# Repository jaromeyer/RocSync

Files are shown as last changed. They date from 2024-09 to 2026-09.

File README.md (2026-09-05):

# RocSync: Temporal Multi-Camera Synchronization

> [!WARNING]
> **This repository is deprecated and no longer maintained.**
> Development has moved to a new fork, which will continue to be updated:
> 👉 **[BAL-ROCS-BUT-COOL/RocSync](https://github.com/BAL-ROCS-BUT-COOL/RocSync)**

RocSync Front

**RocSync**  is an open-source solution for millisecond-accurate temporal synchronization of multiple cameras. The core component is a 25x25 cm PCB featuring 100 dual LEDs (each consisting of a visible red LED and an infrared LED) arranged in a circle and 16 additional dual LEDs to display a binary counter. There is always exactly one illuminated LED in the circle and it advances one step every millisecond, while the binary display counts the number of complete rotations. The second part is a Python application that decodes images and videos of the device and provides exact timestamps (relative to the RocSync device's internal clock) for every frame. It supports synchronization of both standard RGB cameras (e.g., Kinect, GoPro, Canon) and specialized IR tracking cameras, such as the [Atracsys fusionTrack 500](https://atracsys.com/fusiontrack-500/), making it ideal for research and applications requiring high-precision multi-camera setups.

## Repository Structure

This repository contains three main sections, each with its own README:

- **`hw/`**: KiCad files for PCB design and CAD models.
- **`fw/`**: PlatformIO project for microcontroller firmware.
- **`sw/`**: Python source code for computer vision processing.

## Getting Started

For detailed instructions on setting up and using RocSync, please refer to the README files in the respective sections. 

## Credits

- **Frédéric Giraud**: Creator of the initial prototype.
- **Lilian Calvet**: Conceptual designer.

Feel free to explore, contribute, and use RocSync in your projects!

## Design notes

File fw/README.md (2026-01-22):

# RocSync firmware

This folder contains the firmware. It uses platformio with the arduino core for CH32V003. Use their USB debugger to flash the PCB.

# How to build a PlatformIO based project

1. Install PlatformIO Core:
    Go to the [PlatformIO Website](https://docs.platformio.org/en/latest/core/installation/methods/installer-script.html#local-download-macos-linux-windows) and follow the instructions:

    - Download the `get-platformio.py` script (right click -> "save as")
    
    - in a command window got to where the file has beend downloaded to:
        ```shell
        cd <download folder>
        ```

    - run the script (installs PlatformIO core in a new vEnv, path is shown as a message)  
        ```shell
        python get-platformio.py
        ```

2. Activate the PlatformIO vEnv
    
    - the PlatformIO vEnv is usually created under `C:\users\<name>\.platformio\penv`. Navigate to the install location and find the `Scripts` folder.
        ```shell
        cd <...>\.platformio\penv\Scripts
        ```
    
    - activate the vEnv
        ```
        activate
        ```

3. Install support for the CH32V003 chip
    By default, PlatformIO doesn't offer support for the CH32V003 chip. An Arduino-style port of this chips functionality exists in [this repository](https://github.com/Community-PIO-CH32V/platform-ch32v). Follow its installation instructions:

    - the previously created vEnv needs to be activated in a terminal
    
    - install the CH32V003 library through PIO's own package manager: 
        ```shell
        pio pkg install -g -p https://github.com/Community-PIO-CH32V/platform-ch32v.git
        ```

4. Flashing the MC (with PlatformIO)
    To connect the CH32V003 to a computer, the [WCH-LinkE device](https://www.olimex.com/Products/RISC-V/WCH/WCH-LinkE/) is needed. Additionally, the [WCH-Utiliy](https://www.wch.cn/downloads/WCH-LinkUtility_ZIP.html) can be used to test the connection, configure the chip and manually flash binaries to the MC. However, to flash with PlatformIO, the Utility isn't strictly needed:

    - Connect the SWDIO and GND pin of the CH32V003 to the LinkE device (cables should ideally be < 30cm long).
    
    - make sure a battery is connected to the RocSync and it's switched on.

    - the previously created vEnv needs to be activated in a terminal.

    - navigate to a PIO project folder (where the firmware is located in a `src` folder)
        ```shell
        cd <project folder>
        ```
    - to compile and flash the code to the MC use the following command:
        ```shell
        pio run --target upload
        ```

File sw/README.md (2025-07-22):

# RocSync decoding software

This folder contains the Python application for detecting and decoding the RocSync device in videos and images where it is visible.

### How it works:

1. **Find ArUco marker**: Detect the ArUco marker to determine the approximate position and orientation.
2. **Coarse homographic reprojection**: Use the detected marker's corners to perform a coarse homographic reprojection of the image.
3. **Locate corner LEDs**: Identify the corner LEDs in the reprojected image.
4. **Accurate reprojection**: Use the corner LEDs to refine the reprojection for higher accuracy.
5. **Decode LEDs**: Decode the circle and binary counter LEDs by thresholding their general areas to obtain an exact timestamp.
6. **Timestamp fitting**: If the input was a video, perform robust linear regression on all extracted timestamps to reject outliers and estimate timestamps for all frames.

## Installation
To install RocSync as a Python module, run the following commands:

```bash
git clone https://github.com/jaromeyer/RocSync.git
pip install ./RocSync/sw
```

## Usage
```
$ rocsync -h
usage: rocsync [-h] [-c {rgb,ir}] [-s N] [-e DIRECTORY] [-o FILE] [--debug DIRECTORY] PATH [PATH ...]

Extract timestamps from images and videos showing the RocSync device.

positional arguments:
  PATH                  path to a video, image, or directory containing videos and/or images

options:
  -h, --help            show this help message and exit
  -c, --camera_type {rgb,ir}
                        specify the type of camera (default: rgb)
  -s, --stride N        scan every N-th frame only (default: same as framerate, only applies to videos)
  -e, --export_frames DIRECTORY
                        directory to store all raw frames as PNGs with timestamp (only applies to videos)
  -o, --output FILE     JSON file to store results (default: output.json)
  -y, --yes             automatically run yes for all prompts (potentially overwrites existing files)
  --debug DIRECTORY     directory to store debug images (very slow)

  --start1 WINDOW1_START_TIME 
                        specify optional start timestamp for first search window in format hh:mm:ss.ms (default: 00:00:00.0)
  --end1 WINDOW1_END_TIME 
                        specify optional end timestamp for first search window in format hh:mm:ss.ms (default: end of file)

  --start2 WINDOW2_START_TIME 
                        specify optional start timestamp for second search window in format hh:mm:ss.ms (default: none)
  --end2 WINDOW2_END_TIME 
                        specify optional end timestamp for second search window in format hh:mm:ss.ms (default:none)

  --sync_video          automatically time-sync the videos using the estimated timestamps (requires ffmpeg)
  --synced_folder FOLDER 
                        output folder for time-synced videos
  --fps FPS             desired FPS for time-synced videos (default: desired FPS determined from input videos)
  ```

## Example
```
$ rocsync ./examples/h10.MP4 ./examples
Working on ./examples/h10.MP4
Analyzing frames: 100%|████████████████████| 6520/6520 [02:21<00:00, 45.93it/s]
Number of considered frames:                             1888
Number of rejected outliers:                                0
R2 score:                                              1.0000
RMSE:                                                 0.44 ms
First frame:                                       -4333.4 ms
Last frame:                                        22858.4 ms
Expected duration (fps):              27189.7 ms (239.76 fps)
Actual duration (fps):                27191.7 ms (239.74 fps)
Delta (actual - expected)              2.08 ms (0.010% speed)
Exposure time (mean/min/max):               3.97/3.00/5.00 ms
-------------------------------------------------------------
Processing files: 100%|█████████████████████████| 1/1 [02:22<00:00, 142.04s/it]
```

### FFmpeg
To visually inspect the synchronization you can use FFmpeg to combine the aligned videos side-by-side:
```bash
ffmpeg \
	-ss 4.2803 -i video1.mp4 \
	-ss -8.1024 -i video2.mp4 \
	-filter_complex "[0:v]setpts=PTS*1.000020938577059[v0];[1:v]setpts=PTS*1.000083866934668[v1];[v0][v1]hstack=inputs=2" \
	-c:v h264_nvenc \
	-preset p1 \
	-r 30 \
	synchronized.mp4
```

## Ideas for future improvements
- [ ] Write debug images in separate thread to not slow down the main processing
- [ ] Implement additional filters for the IR pipeline (e.g., uniform corner distance)
- [ ] Implement movement filter to reject frames with motion blur
- [ ] Use partial ring LED intensity to determine sub-millisecond timestamps (e.g., compute distance to min and max detected intensity)
- [ ] Use gray code and partial LED detection to decode the counter even when it changed during the exposure

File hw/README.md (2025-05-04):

# RocSync hardware
This folder contains the KiCad project for the RocSync device. It was designed with manufacturing and assembly by JLCPCB in mind. The following [plugin](https://github.com/Bouni/kicad-jlcpcb-tools) was used to generate fabrication files for JLCPCB. The folder `3d_models` contains the STEP and STL files for the cover and handle.

## TODO
- [ ] Use TCXO for better accuracy (e.g., [TX0283D](https://jlcpcb.com/partdetail/Tst-TX0283D/C499191))
- [ ] Decouple IR and visible LED brightness
- [ ] Fix decreasing brightness when battery voltage is low (e.g., by adding a buck-boost converter)
- [ ] Extend counter for longer recordings or displaying custom experiment identifier
- [ ] Add human readable display for convenience (e.g., OLED, 7-segment LED)
- [ ] Add 5th static IR-LED to make rotation unambiguous

## Mechanical BOM
| Part                        | Quantity | Source                                                              |
| --------------------------- | -------- | ------------------------------------------------------------------- |
| 604050 battery              | 1        | [Aliexpress](https://www.aliexpress.com/item/1005007605225540.html) |
| Handle                      | 1        | 3d printed                                                          |
| Cover                       | 1        | 3d printed                                                          |
| M3x10 screws                | 4        | [Aliexpress](https://www.aliexpress.com/item/32850409234.html)      |
| M3 nuts                     | 4        | [Aliexpress](https://www.aliexpress.com/item/32977174437.html)      |
| matte smoked film ~32x32 cm | 1        | [Aliexpress](https://www.aliexpress.com/item/1005005636607163.html) |

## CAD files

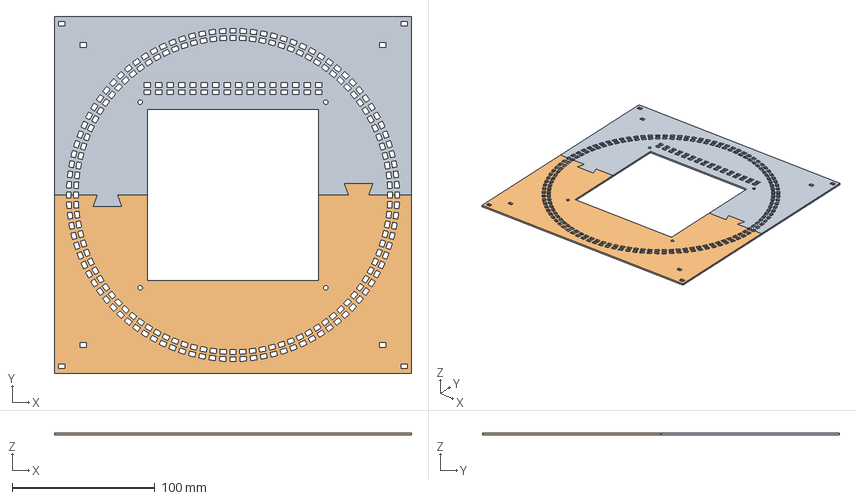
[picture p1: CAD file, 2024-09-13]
hw/3d_models/cover.step
250.0 x 250.0 x 1.60 mm

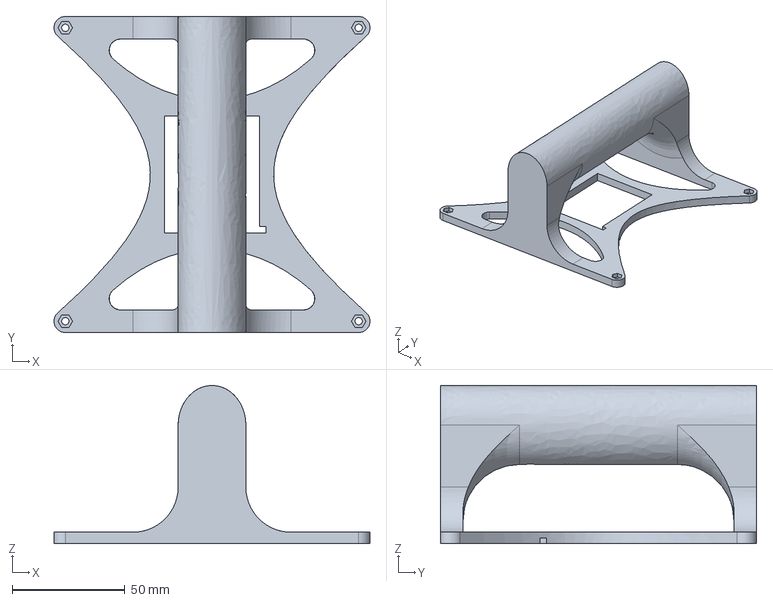
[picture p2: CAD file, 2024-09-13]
hw/3d_models/handle.step
140.0 x 140.0 x 70.0 mm

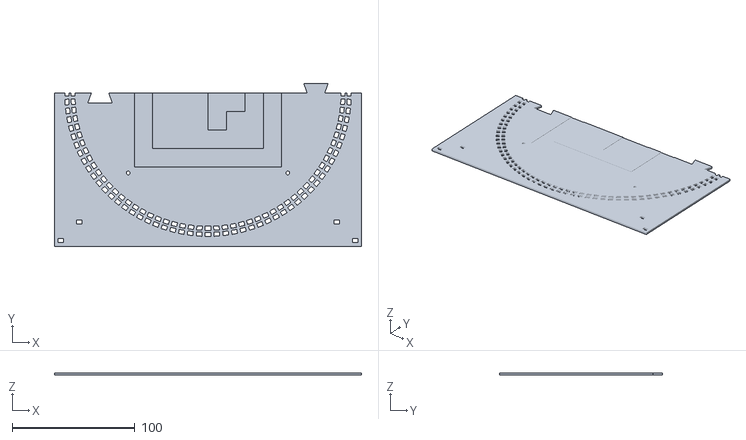
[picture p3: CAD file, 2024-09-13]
hw/3d_models/cover_bottom.stl
250.0 x 133.0 x 2.00

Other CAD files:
hw/3d_models/cover_top.stl
hw/3d_models/RocSync.f3d
hw/3d_models/handle.stl

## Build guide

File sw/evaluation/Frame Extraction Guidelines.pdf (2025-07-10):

Frame Extraction Guidelines

What is needed to extract the frames?
- time_synchronization.json file: results of the synchronization (more details below)
- clips_config.json file: time windows for which frames should be extracted
- extract_clips_as_png.py: script to extract the synchronized frames
- raw video data

Results of the synchronization: time_synchronization.json
- To use the frame extraction script, make sure that the path to the videos, i.e., the key of the dictionary, is adjusted to where they are actually stored
- The temporal synchronization follows the relation y = mx + b where x is the frame number, y is the aligned timestamp, b is the temporal offset and m is the temporal drift (including the compensation for different fps)
- The most important quantities in the file are "n_frames" (number of frames in the recording), "measured_fps" (actual fps from the recording), "first_frame" corresponds to the offset b and is in ms, and "last_frame" which is used to calculate the slope m as m = (last_frame-first_frame)/n_frames
- All other quantities are simply there for debugging and statistics of the temporal synchronization to check how well it worked
- This file should be stored within the calibration folder

One step before frames can be extracted:
- Choose one camera recording and identify the time window during which you want to extract the frames.
- Add this time window to the clips_config.json file

How to extract synchronized frames?
- For this exists a standalone script called "extract_clips_as_png.py"
- Verify in line 27 that the path is correct and especially that the name of the temporal synchronization .json file matches as well
- The general command to use the script is as follows:
python path/to/extract_clips_as_png.py --dataset_folder path/to/dataset_folder --clips_to_extract_json path/to/clips_config.json --target_fps desired_fps --from_raw_camera_time_of_camera cameraX
- The dataset folder is the location where the calibration folder is located. CameraX should be replaced by the name of the actual recording used to choose the time windows of which frames should be extracted.
- Running this script creates a new folder "synced_clips_pngs" in the same location as the dataset folder that contains a single folder for each time window (folder name corresponds to the aligned timestamp) which also contains a single folder for each camera with all extracted frames
- If you want to look at the light switch to verify the synchronization you need to keep in mind that the light source we used is not ideal. It turns on gradually and also increases gradually in brightness. So, what I did is to look at the last large increase in brightness.

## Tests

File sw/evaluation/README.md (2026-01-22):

# Multi-Camera Sync Toolkit
## 📂 Folder Setup

Your dataset folder should look like this:

```
dataset_folder/
├── raw_videos/
│   ├── camera1_raw.mp4
│   ├── camera2_raw.mp4
│   ├── camera3_raw.mp4
│   └── ...
│
└── time sync/
    ├── clips_config.json
    ├── time_synchronization.json
    ├── extract_synced_videos.py
    ├── extract_clips_as_png.py
    ├── check_time_sync_all.py
    └── ...
```

### Description:

* **`raw_videos/`** – contains all raw camera recordings (e.g., `.mp4`, `.MOV`).
* **`time sync/`** – contains synchronization files:

  * `clips_config.json`: defines which clips to extract.
  * `time_synchronization_*.json`: contains timing information for each camera.

---

## ✅ Check synchronization of all clips

Once you have a finished `time_synchronization_*.json` file, check if all videos have been synchronized correctly by the RocSync script and/or the manual synchronization. Check a moment near the beginning of the Recording and a moment near the end of the Recording to make sure there is no drift. Run this before synchronizing huge datasets, it will save you a lot of time down the road.

Run the script:
```bash
python path/to/check_time_sync_all.py \
    --time HH:MM:SS.mmm \
    --from-camera "cameraX"
```

### Arguments:

* `--time`
  The time of the reference video you want to display in this format: HH:MM:SS.mmm.

* `--from-camera`
  Name of the reference camera (e.g., `"camera1_raw"` or `"gopro7_raw"`) — this camera’s timing is used as the reference for synchronization.

---

## 🎥 Extract Synced Videos

This guide explains how to organize your dataset and run the `extract_synced_videos.py` script to generate **time-synchronized video clips** from multiple cameras.

### 🧭 Usage

Run the extraction script from your terminal:

```bash
python extract_synced_videos.py 
```

### Optional Arguments:

* `--dataset-folder`
  Path to your dataset folder (the one containing `raw_videos/` and `time sync/`). Not necessary if you follow the **folder setup** above.

* `--target-fps`
  Desired output frame rate (e.g., 30).

* `--from-camera`
  Name of the reference camera (e.g., `"camera1_raw"` or `"gopro7_raw"`) — this camera’s timing is used as the reference for synchronization.

* `--time-sync-json`
  Path to your `time_synchronization_*.json` file

* `--clips-json`
  Path to the `clips_config.json` file

* `--ignore-overlap`
  If set, the script will not restrict synchronization to the time interval shared by **all** files (the global overlap).  
  Use this if some videos do **not** cover the requested timestamp/time range (e.g., some cameras started later or stopped earlier).
### Output:
* Folder called synced_videos with the syncronized clips

## 📷 Extract Synced Frames
This guide explains how to organize your dataset and run the `extract_clips_as_png.py` script to generate **time-synchronized pictures** from multiple cameras.

### 🧭 Usage

Run the script from your terminal:

```bash
python extract_clips_as_png.py 
```

### Optional Arguments:

* `--dataset-folder`
  Path to your dataset folder (the one containing `raw_videos/` and `time sync/`). Not necessary if you follow the **folder setup** above.

* `--target-fps`
  Desired output frame rate (e.g., 30).

* `--from-camera`
  Name of the reference camera (e.g., `"camera1_raw"` or `"gopro7_raw"`) — this camera’s timing is used as the reference for synchronization.

* `--time-sync-json`
  Path to your `time_synchronization_*.json` file

* `--clips-json`
  Path to the `clips_config.json` file

* `--only-specified`
  If set, only produce PNGs for the camera given by `--from-camera`.

### Output:
* Folder called synced_clips_png with the synchronized png frames

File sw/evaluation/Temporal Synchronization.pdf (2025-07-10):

Temporal Synchronization

What is temporal synchronization?
- Aligning several video streams such that it is frame-accurate
- This then allows to extract frames which are the basis / inputs for computer vision models
- Aligning means fitting a linear function y = mx + b where x is the frame index, y the aligned timestamp, m incorporates the temporal drift and b the temporal offset
- The offset b is due to the shifted start of the recording of each camera
- The temporal drift m is due to slight variations in the internal clocks of the cameras (while the drift itself is very small, it's still necessary to account for it to have a frame-accurate synchronization)

How is the fitting performed (what's happening in the code)?
- To get the x and y values the RocSync is used (ideally shown at the start and end of a recording)
- RocSync: ARuCo marker in the center, 4 LEDs at the corners, 100 LEDs in a circle (100ms), counter of these revolutions in binary as a line above the ARuCo marker. Additionally, infrared sources for infrared cameras (Atracsys)
- Basic principle: Each frame is analyzed w.r.t. whether the ARuCo marker is seen or not. If it's seen then the 4 LEDs are used to translate and rotate the RocSync such that it's positioned head-on. Then the binary number of revolutions is read off to get the actual timestamp. Moreover, the circle segment of LEDs is used to get the exposure time. The actual timestamp is then our y and the frame number that led to this timestamp is our x.
- After a RANSAC regressor is used to perform a fit on the data and from this m and b can be deduced.

How is the fitting performed (as a user)?
- To save some time (the algorithm doesn't need to check each frame of a whole recording), it's better to first analyze all recordings to check when the RocSync is shown. Usually these are two time windows. Since the time windows are equal for all cameras of one recording, the time windows need to be large enough such that the RocSync is seen on each camera.
- Identify cameras that have low brightness and write name fragments of these cameras in the main.py file in line 357 such that the brightness is increased
- After this pre-processing step, the following command line prompt is used: rocsync path/to/data --start1 hh:mm:ss --end1 hh:mm:ss --start2 hh:mm:ss --end2 hh:mm:ss -o path/to/output.json
- In practice this command looks like this:
rocsync F:/visceral_v1 --start1 00:00:00 --end1 00:15:00 --start2 01:00:00 --end2 01:15:00 -o
F:/visceral_v1/calibration/time_synchronization_RecX.json

- Make sure to use the newest commit of Jaro's code directly in the RocSync repository and not the forked version in the calibration repo of the BAL-ROCS-BUT-COOL organization.

Structure of the output .json file (dictionary) only most important explanations:
Key – location of camera X
Value – {"n_frames": number of frames of recording
"n_considered_frames" and "n_rejected_frames": frames that were considered for the fit vs frames that were outliers
"measured_fps": self-explanatory
"speed_factor": gives a relative feeling of how strong the drift of a certain camera is
"first_frame": temporal offset b in ms
"last_frame": in ms, used with "first_frame" and "n_frames" to calculate the temporal drift m via (last_frame-first_frame)/n_frames}

How to check the synchronization?
- Usually there should be two light switches visible in a recording
- Choose one camera and identify the two time windows of around 5-10 seconds during which the light switch happens (if possible choose a light switch of the whole room rather than only the OR lamp (see below for details))
- Use the extract_clips_as_png.py script in the calibration repository to extracted synchronized frames:
- Line 27: change the name of the synchronization file (ToDo -> implement such that it can be passed via command line argument)
- Create a file clips_config.json that looks like this:
[
{
"start": "00:05:15.000",
"end": "00:05:25.000"
},
{
"start": "01:06:45.000",
"end": "01:06:55.000"
}
]
- Via the command line input the following prompt:
python further_scripts/extract_clips_as_png.py --dataset_folder path/to/dataset_folder --clips_to_extract_json path/to/clips_config.json --target_fps 30 --from_raw_camera_time_of_camera camera_used_for_clips_config
- This gives a new folder called "synced_clips_png" in the location of the dataset folder
- Navigate to the "synced_clips_png" folder and go to the camera folder of the one used for the clips_config.json. Identify two frames between which the light switch happens. This step is not straightforward with the current datasets, since the light switch is gradual and not immediate. Therefore, there might be some faint light already for some cameras while for others it is still dark. For the room light -> choose the frames where the room has no dark patches anymore. For the OR lamp -> Try to identify the strongest brightness increase.
- Check all cameras if for the given frames the same change in light is seen (if it's more than one frame off, it's clear something went wrong; if it's only one frame off, look closely as it might be not due to the synchronization but the light source itself and therefore it could be that there is no issue)

Common Issues:
- Near field cameras are usually low in brightness -> adjusting brightness might help
- If the ChAruCo board and the RocSync are visible at the same time the wrong AruCo marker might be chosen (but this should be fixed in the newest commit)
- If cameras are zoomed in too far the RocSync might not be visible completely
- Binary clock is not readable
- The RocSync is only shown for few frames or from too far away
- The cameras were shut off too early (then simply choose another moment to compare these cameras, usually egocentric cameras and Aria glasses)
- The cameras shut off early due to empty battery
- Due to some (yet) unknown reasons, the synchronization for the Canon cameras and ZedMini seems harder

Manual synchronization procedure:
- In case where there is no solution for the above issues, it's easiest to perform a manual synchronization and look at the cause to the issue later
- For this, two correspondences need to be found (one at the start and one at the end of the video). The first correspondence is usually the first light switch already used to check the synchronization. The second one is ideally also a light switch. In the case of a camera running out of battery or an egocentric camera, some other correspondence is needed (fast movement, audio, etc.)
- Use the Manual_Temp_Synch.py script to perform the manual synchronization:
- Create a new time_synchronization.json file where only the cameras are included that are frame-accurately synched.
- folder1 and folder2 names correspond to the two folders of the temporal synchronization check in "synched_clips_png".
- Change the name of the synchronization json file for the cam_info variable
- From the temporal synchronization check you already know the frame number where the transition of the light brightness happened, i.e., light switch happens between x1 and x2. For both light switches, remember x1 and change it for the y_values_switch variables as x_user.

- Change the camera_name to the desired one that should be manually synched.
- Change the folder name and the time windows in the detect_light_switch_frames function during which the correspondence happens. If the correspondence is a light switch, it usually works with the given code. If the correspondence is not a light switch, make sure, that the correspondence happens in the middle of your time window and you need to input light_switch = False. It may be necessary in that case to increase the number of pre and post frames extracted from the middle of the time window to see the correspondence.
- Run the script. It will output two folders with extracted frames. Ideally the desired correspondence is seen in these frames. If not, change the number of frames extracted before and after the increase in brightness happens or of the other correspondence.
- Now you have to match the frame of the new folder with the one from the synchronization check. Note down the frame number of the camera for which the manual synchronization is performed (x1_cam and x2_cam).
- Run the script again. Now the script extracts all actual timestamps for all cameras that are synched perfectly (y's) and the x's are x1_cam and x2_cam. Then a robust regression is performed to get the new fit.
- Now you can add a new entry to the time_synchronization.json file where especially the speed_factor, first_frame, n_frames, measured_fps, last_frame is needed.
- To check if you did the manual synchronization correctly, perform the extraction of frames again. If it's not yet fully synched, slightly shift x1_cam or x2_cam respectively, perform the fit again, and check again.

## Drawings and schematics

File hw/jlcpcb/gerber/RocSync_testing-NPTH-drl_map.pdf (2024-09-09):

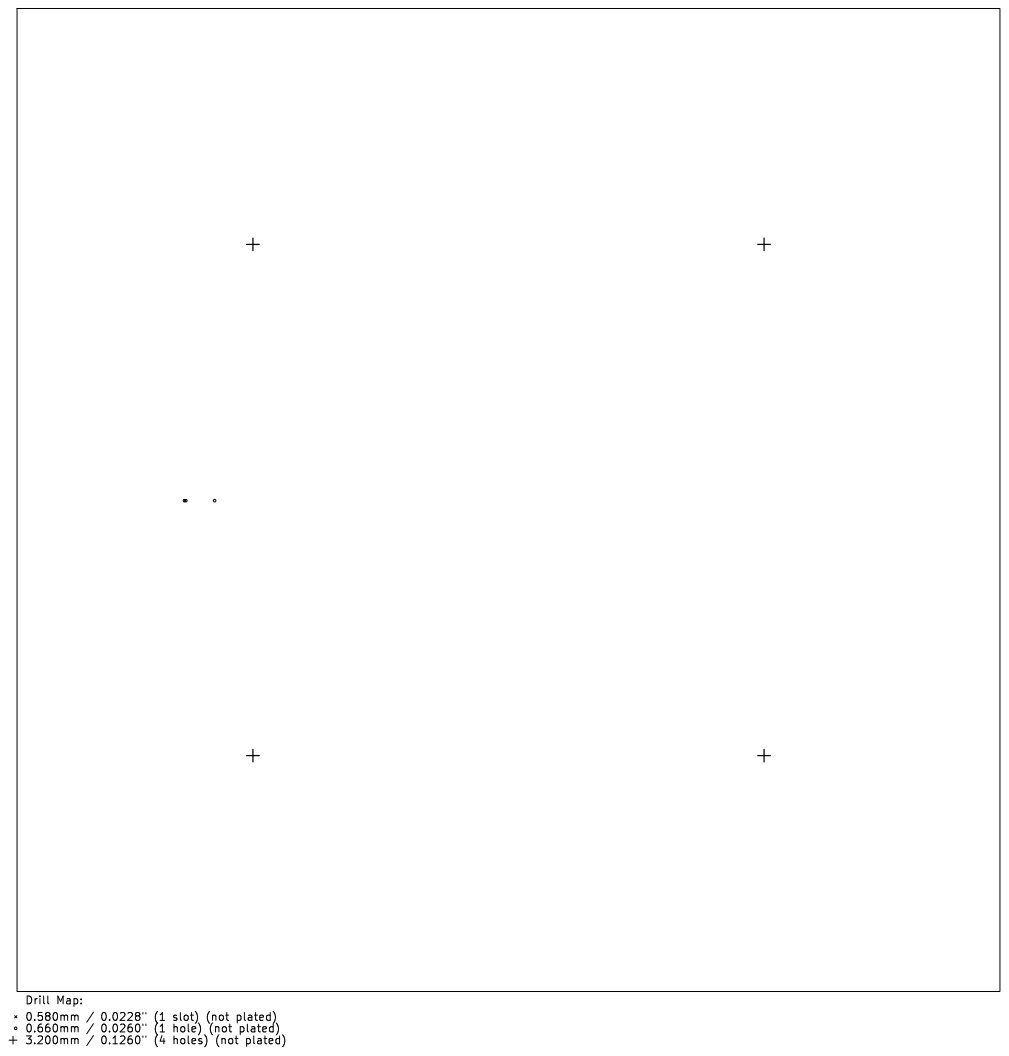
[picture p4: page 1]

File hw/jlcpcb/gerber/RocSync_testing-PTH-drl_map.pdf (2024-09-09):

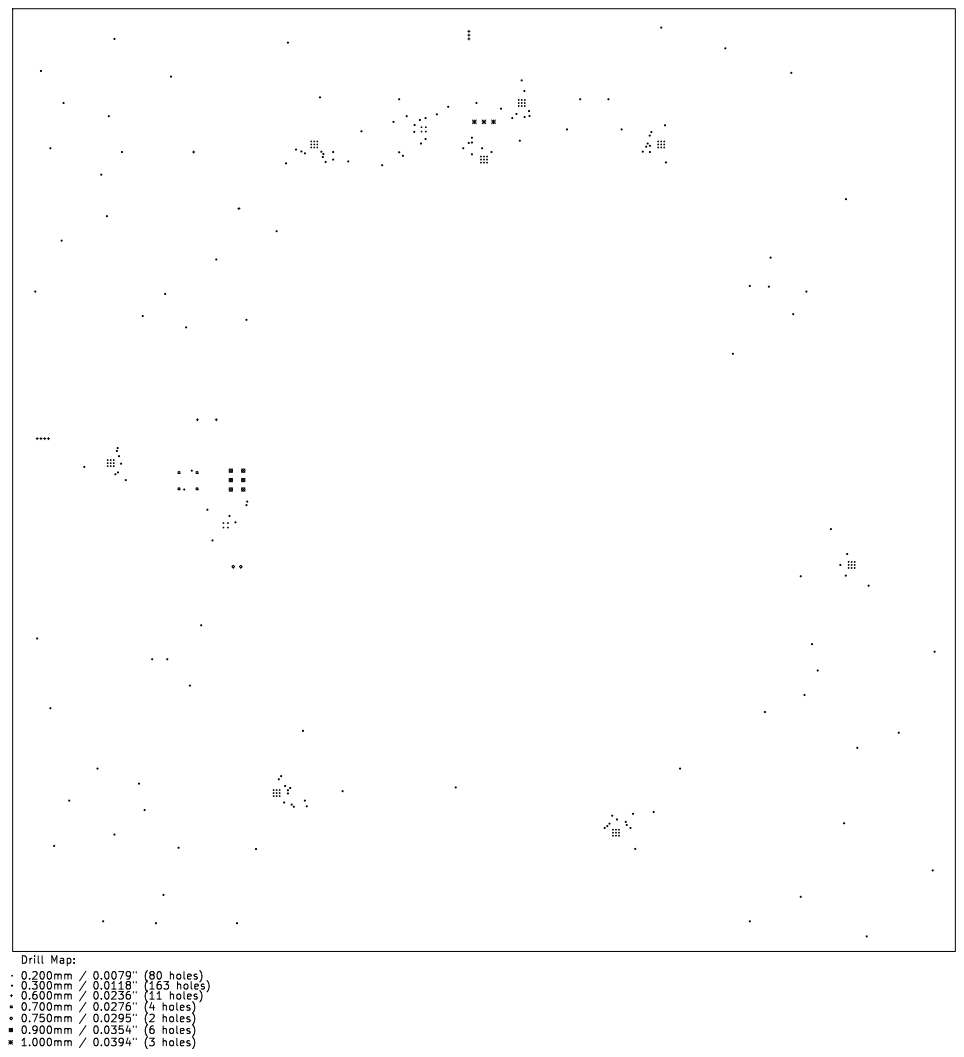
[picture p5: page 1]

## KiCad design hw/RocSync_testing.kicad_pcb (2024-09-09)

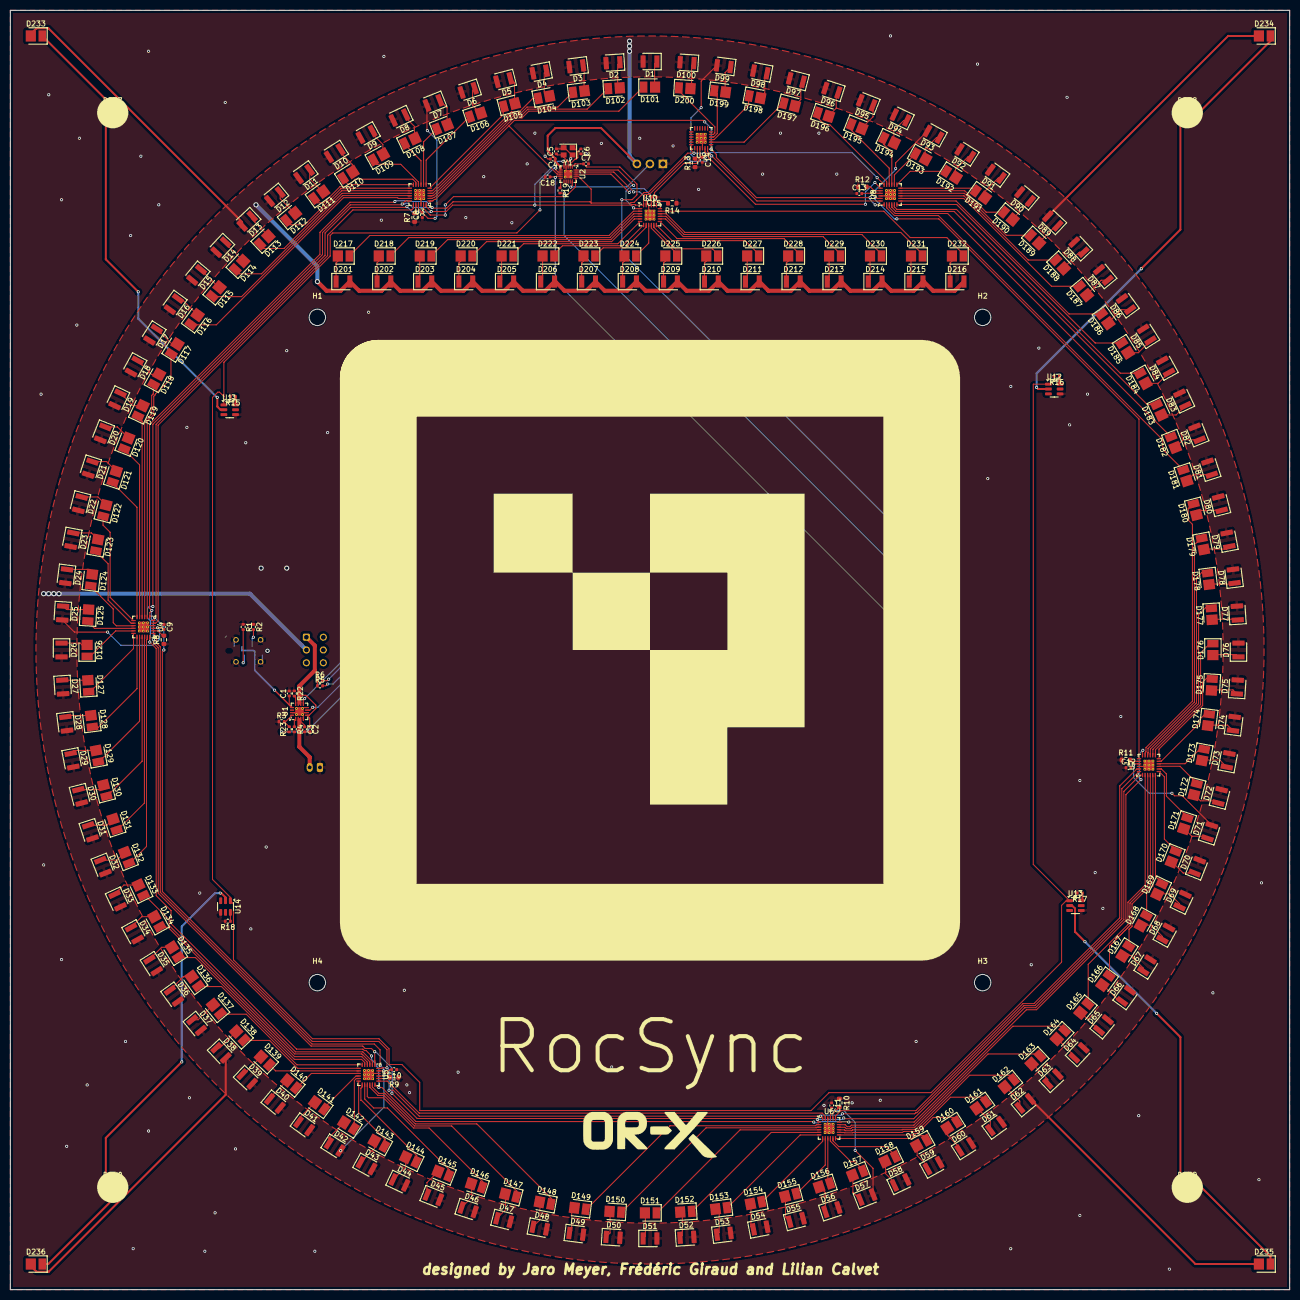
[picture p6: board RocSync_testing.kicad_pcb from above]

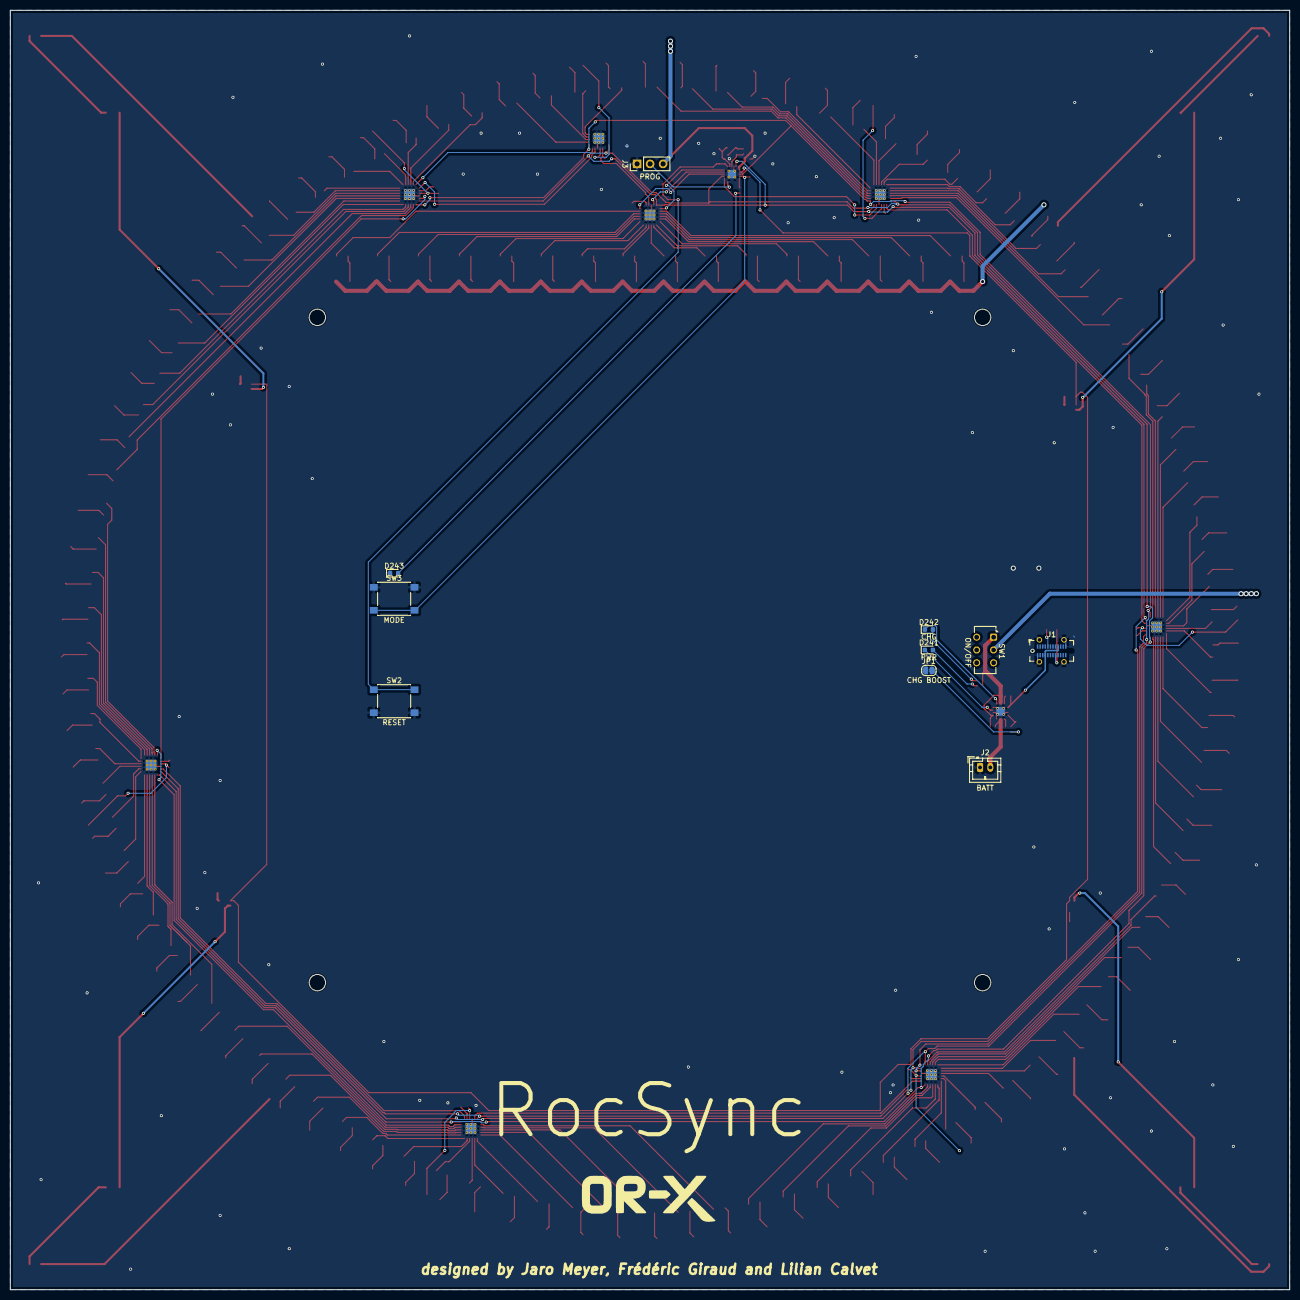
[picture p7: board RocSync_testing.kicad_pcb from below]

Board: 2 copper layers, 250.0 x 250.0 mm, 306 parts (10 on the bottom side), 288 nets.

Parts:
C1: 1uf; C_0402_1005Metric
C2, C3: 4.7uf; C_0402_1005Metric
C4, C7, C8, C9, C10, C11, C12, C13, C14, C15, C18: 0.1uf; C_0402_1005Metric
C5, C6: 10pf; C_0402_1005Metric
D1, D2, D3, D4, D5, D6, D7, D8, D9, D10, D11, D12, D13, D14, D15, D16, D17, D18, D19, D20, D21, D22, D23, D24, D25, D26, D27, D28, D29, D30, D31, D32, D33, D34, D35, D36, D37, D38, D39, D40, D41, D42, D43, D44, D45, D46, D47, D48, D49, D50, D51, D52, D53, D54, D55, D56, D57, D58, D59, D60, D61, D62, D63, D64, D65, D66, D67, D68, D69, D70, D71, D72, D73, D74, D75, D76, D77, D78, D79, D80, D81, D82, D83, D84, D85, D86, D87, D88, D89, D90, D91, D92, D93, D94, D95, D96, D97, D98, D99, D100, D201, D202, D203, D204, D205, D206, D207, D208, D209, D210, D211, D212, D213, D214, D215, D216, D237, D238, D239, D240: LED; HL-A-3528
D101, D102, D103, D104, D105, D106, D107, D108, D109, D110, D111, D112, D113, D114, D115, D116, D117, D118, D119, D120, D121, D122, D123, D124, D125, D126, D127, D128, D129, D130, D131, D132, D133, D134, D135, D136, D137, D138, D139, D140, D141, D142, D143, D144, D145, D146, D147, D148, D149, D150, D151, D152, D153, D154, D155, D156, D157, D158, D159, D160, D161, D162, D163, D164, D165, D166, D167, D168, D169, D170, D171, D172, D173, D174, D175, D176, D177, D178, D179, D180, D181, D182, D183, D184, D185, D186, D187, D188, D189, D190, D191, D192, D193, D194, D195, D196, D197, D198, D199, D200, D217, D218, D219, D220, D221, D222, D223, D224, D225, D226, D227, D228, D229, D230, D231, D232, D233, D234, D235, D236: IR LED; XYC-HIR76C-LX4
D241: PWR; LED_0603_1608Metric
D242: CHG; LED_0603_1608Metric
D243: MODE; LED_0603_1608Metric
H1, H2, H3, H4: MountingHole; MountingHole_3.2mm_M3
J1: USB_C_Receptacle_PowerOnly_6P; USB_C_Receptacle_GCT_USB4115-03-C
J2: BATT; JST_PH_B2B-PH-K_1x02_P2.00mm_Vertical
J3: PROG; PinHeader_1x03_P2.54mm_Vertical
JP1: CHG BOOST; SolderJumper-2_P1.3mm_Open_RoundedPad1.0x1.5mm
R1, R2: 5.1k; R_0402_1005Metric
R3: 2k; R_0402_1005Metric
R4: 10k; R_0402_1005Metric
R5, R6, R19: 1.5k; R_0402_1005Metric
R7, R8, R9, R10, R11, R12, R13, R14: 2.7k; R_0603_1608Metric
R15, R16, R17, R18: 100; R_0402_1005Metric
R22, R23: 1.18k; R_0402_1005Metric
SW1: ON/OFF; SW_CK_JS202011CQN_DPDT_Straight
SW2: RESET; SW_Push_1P1T_NO_6x6mm_H9.5mm
SW3: MODE; SW_Push_1P1T_NO_6x6mm_H9.5mm
U1: BQ24075RGT; VQFN-16-1EP_3x3mm_P0.5mm_EP1.68x1.68mm_ThermalVias
U2: CH32V003FxUx; QFN-20-1EP_3x3mm_P0.4mm_EP1.65x1.65mm_ThermalVias
U3, U4, U5, U6, U7, U8, U9, U10: TLC59283; Texas_RGE0024C_VQFN-24-1EP_4x4mm_P0.5mm_EP2.1x2.1mm_Thermal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
U11, U12, U13, U14: BCR420UW6Q; SOT-23-6
Y1: Crystal_GND24; Crystal_SMD_2520-4Pin_2.5x2.0mm

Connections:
+BATT: C3.1, J2.2, U1.2 (BAT), U1.3 (BAT)
/CLK: U2.5 (PD0), U3.24 (SCLK), U4.24 (SCLK), U5.24 (SCLK), U6.24 (SCLK), U7.24 (SCLK), U8.24 (SCLK), U9.24 (SCLK), U10.24 (SCLK)
/CORNER_PWM: U2.7 (PC0), U11.1 (EN), U12.1 (EN), U13.1 (EN), U14.1 (EN)
/COUNTER_BLANK: U2.18 (PD4), U10.18 (BLANK)
/COUNTER_DATA: U2.19 (PD5), U10.23 (SIN)
/COUNTER_LATCH: U2.20 (PD6), U10.1 (LAT)
/OSCI: C6.1, U2.2 (PA1), Y1.1
/OSCO: C5.1, U2.3 (PA2), Y1.3
/RING_BLANK: U2.17 (PD3), U3.18 (BLANK), U4.18 (BLANK), U5.18 (BLANK), U6.18 (BLANK), U7.18 (BLANK), U8.18 (BLANK), U9.18 (BLANK)
/RING_DATA: U2.16 (PD2), U3.23 (SIN)
/RING_LATCH: U2.8 (PC1), U3.1 (LAT), U4.1 (LAT), U5.1 (LAT), U6.1 (LAT), U7.1 (LAT), U8.1 (LAT), U9.1 (LAT)
/Ring LEDs 1-16/DOUT: U3.19 (SOUT), U4.23 (SIN)
/Ring LEDs 17-32/DOUT: U4.19 (SOUT), U5.23 (SIN)
/Ring LEDs 33-48/DOUT: U5.19 (SOUT), U6.23 (SIN)
/Ring LEDs 49-64/DOUT: U6.19 (SOUT), U7.23 (SIN)
/Ring LEDs 65-80/DOUT: U7.19 (SOUT), U8.23 (SIN)
/Ring LEDs 81-96/DOUT: U8.19 (SOUT), U9.23 (SIN)
/SWDIO: J3.2, U2.15 (PD1)
GND: C1.2, C2.2, C3.2, C4.2, C5.2, C6.2, C7.2, C8.1, C9.1, C10.1, C11.1, C12.1, C13.1, C14.2, C15.1, C18.2, D243.1 (K), J1.A12 (GND), J1.B12 (GND), J1.S1 (SHIELD), J2.1, J3.1, JP1.1 (A), R1.1, R2.1, R3.1, R4.2, R7.1, R8.1, R9.1, R10.1, R11.1, R12.1, R13.1, R14.1, R15.2, R16.2, R17.2, R18.2, R22.1, SW2.2, SW3.1, U1.4 (~CE), U1.6 (EN1), U1.8 (VSS), U1.15 (SYSOFF), U1.17 (VSS), U2.4 (VSS), U2.21 (VSS), U3.22 (GND), U3.25 (PowerPAD), U4.22 (GND), U4.25 (PowerPAD), U5.22 (GND), U5.25 (PowerPAD), U6.22 (GND), U6.25 (PowerPAD), U7.22 (GND), U7.25 (PowerPAD), U8.22 (GND), U8.25 (PowerPAD), U9.22 (GND), U9.25 (PowerPAD), U10.22 (GND), U10.25 (PowerPAD), U11.4 (GND), U12.4 (GND), U13.4 (GND), U14.4 (GND), Y1.2, Y1.4
unnamed: D1.1 (K), D101.2 (A)
unnamed: D10.1 (K), D110.2 (A)
unnamed: D11.1 (K), D111.2 (A)
unnamed: D100.1 (K), D200.2 (A)
unnamed: D101.1 (K), U3.2 (OUT0)
unnamed: D2.1 (K), D102.2 (A)
unnamed: D102.1 (K), U3.3 (OUT1)
unnamed: D3.1 (K), D103.2 (A)
unnamed: D103.1 (K), U3.4 (OUT2)
unnamed: D4.1 (K), D104.2 (A)
unnamed: D104.1 (K), U3.5 (OUT3)
unnamed: D5.1 (K), D105.2 (A)
unnamed: D105.1 (K), U3.6 (OUT4)
unnamed: D6.1 (K), D106.2 (A)
unnamed: D106.1 (K), U3.7 (OUT5)
unnamed: D7.1 (K), D107.2 (A)
unnamed: D107.1 (K), U3.8 (OUT6)
unnamed: D8.1 (K), D108.2 (A)
unnamed: D108.1 (K), U3.9 (OUT7)
unnamed: D9.1 (K), D109.2 (A)
unnamed: D109.1 (K), U3.10 (OUT8)
unnamed: D110.1 (K), U3.11 (OUT9)
unnamed: D111.1 (K), U3.12 (OUT10)
unnamed: D12.1 (K), D112.2 (A)
unnamed: D112.1 (K), U3.13 (OUT11)
unnamed: D13.1 (K), D113.2 (A)
unnamed: D113.1 (K), U3.14 (OUT12)
unnamed: D14.1 (K), D114.2 (A)
unnamed: D114.1 (K), U3.15 (OUT13)
unnamed: D15.1 (K), D115.2 (A)
unnamed: D115.1 (K), U3.16 (OUT14)
unnamed: D16.1 (K), D116.2 (A)
unnamed: D116.1 (K), U3.17 (OUT15)
unnamed: D17.1 (K), D117.2 (A)
unnamed: D117.1 (K), U4.2 (OUT0)
unnamed: D18.1 (K), D118.2 (A)
unnamed: D118.1 (K), U4.3 (OUT1)
unnamed: D19.1 (K), D119.2 (A)
unnamed: D119.1 (K), U4.4 (OUT2)
unnamed: D20.1 (K), D120.2 (A)
unnamed: D120.1 (K), U4.5 (OUT3)
unnamed: D21.1 (K), D121.2 (A)
unnamed: D121.1 (K), U4.6 (OUT4)
unnamed: D22.1 (K), D122.2 (A)
unnamed: D122.1 (K), U4.7 (OUT5)
unnamed: D23.1 (K), D123.2 (A)
unnamed: D123.1 (K), U4.8 (OUT6)
unnamed: D24.1 (K), D124.2 (A)
unnamed: D124.1 (K), U4.9 (OUT7)
unnamed: D25.1 (K), D125.2 (A)
unnamed: D125.1 (K), U4.10 (OUT8)
unnamed: D26.1 (K), D126.2 (A)
unnamed: D126.1 (K), U4.11 (OUT9)
unnamed: D27.1 (K), D127.2 (A)
unnamed: D127.1 (K), U4.12 (OUT10)
unnamed: D28.1 (K), D128.2 (A)
unnamed: D128.1 (K), U4.13 (OUT11)
unnamed: D29.1 (K), D129.2 (A)
unnamed: D129.1 (K), U4.14 (OUT12)
unnamed: D30.1 (K), D130.2 (A)
unnamed: D130.1 (K), U4.15 (OUT13)
unnamed: D31.1 (K), D131.2 (A)
unnamed: D131.1 (K), U4.16 (OUT14)
unnamed: D32.1 (K), D132.2 (A)
unnamed: D132.1 (K), U4.17 (OUT15)
unnamed: D33.1 (K), D133.2 (A)
unnamed: D133.1 (K), U5.2 (OUT0)
unnamed: D34.1 (K), D134.2 (A)
unnamed: D134.1 (K), U5.3 (OUT1)
unnamed: D35.1 (K), D135.2 (A)
unnamed: D135.1 (K), U5.4 (OUT2)
unnamed: D36.1 (K), D136.2 (A)
unnamed: D136.1 (K), U5.5 (OUT3)
unnamed: D37.1 (K), D137.2 (A)
unnamed: D137.1 (K), U5.6 (OUT4)
unnamed: D38.1 (K), D138.2 (A)
unnamed: D138.1 (K), U5.7 (OUT5)
unnamed: D39.1 (K), D139.2 (A)
unnamed: D139.1 (K), U5.8 (OUT6)
unnamed: D40.1 (K), D140.2 (A)
unnamed: D140.1 (K), U5.9 (OUT7)
unnamed: D41.1 (K), D141.2 (A)
unnamed: D141.1 (K), U5.10 (OUT8)
unnamed: D42.1 (K), D142.2 (A)
unnamed: D142.1 (K), U5.11 (OUT9)
unnamed: D43.1 (K), D143.2 (A)
unnamed: D143.1 (K), U5.12 (OUT10)
unnamed: D44.1 (K), D144.2 (A)
unnamed: D144.1 (K), U5.13 (OUT11)
unnamed: D45.1 (K), D145.2 (A)
unnamed: D145.1 (K), U5.14 (OUT12)
unnamed: D46.1 (K), D146.2 (A)
unnamed: D146.1 (K), U5.15 (OUT13)
unnamed: D47.1 (K), D147.2 (A)
unnamed: D147.1 (K), U5.16 (OUT14)
unnamed: D48.1 (K), D148.2 (A)
unnamed: D148.1 (K), U5.17 (OUT15)
unnamed: D49.1 (K), D149.2 (A)
unnamed: D149.1 (K), U6.2 (OUT0)
unnamed: D50.1 (K), D150.2 (A)
unnamed: D150.1 (K), U6.3 (OUT1)
unnamed: D51.1 (K), D151.2 (A)
unnamed: D151.1 (K), U6.4 (OUT2)
unnamed: D52.1 (K), D152.2 (A)
unnamed: D152.1 (K), U6.5 (OUT3)
unnamed: D53.1 (K), D153.2 (A)
unnamed: D153.1 (K), U6.6 (OUT4)
unnamed: D54.1 (K), D154.2 (A)
unnamed: D154.1 (K), U6.7 (OUT5)
unnamed: D55.1 (K), D155.2 (A)
unnamed: D155.1 (K), U6.8 (OUT6)
unnamed: D56.1 (K), D156.2 (A)
unnamed: D156.1 (K), U6.9 (OUT7)
unnamed: D57.1 (K), D157.2 (A)
unnamed: D157.1 (K), U6.10 (OUT8)
unnamed: D58.1 (K), D158.2 (A)
unnamed: D158.1 (K), U6.11 (OUT9)
unnamed: D59.1 (K), D159.2 (A)
unnamed: D159.1 (K), U6.12 (OUT10)
unnamed: D60.1 (K), D160.2 (A)
unnamed: D160.1 (K), U6.13 (OUT11)
unnamed: D61.1 (K), D161.2 (A)
unnamed: D161.1 (K), U6.14 (OUT12)
unnamed: D62.1 (K), D162.2 (A)
unnamed: D162.1 (K), U6.15 (OUT13)
unnamed: D63.1 (K), D163.2 (A)
unnamed: D163.1 (K), U6.16 (OUT14)
unnamed: D64.1 (K), D164.2 (A)
unnamed: D164.1 (K), U6.17 (OUT15)
unnamed: D65.1 (K), D165.2 (A)
unnamed: D165.1 (K), U7.2 (OUT0)
unnamed: D66.1 (K), D166.2 (A)
unnamed: D166.1 (K), U7.3 (OUT1)
unnamed: D67.1 (K), D167.2 (A)
unnamed: D167.1 (K), U7.4 (OUT2)
unnamed: D68.1 (K), D168.2 (A)
unnamed: D168.1 (K), U7.5 (OUT3)
unnamed: D69.1 (K), D169.2 (A)
unnamed: D169.1 (K), U7.6 (OUT4)
unnamed: D70.1 (K), D170.2 (A)
unnamed: D170.1 (K), U7.7 (OUT5)
unnamed: D71.1 (K), D171.2 (A)
unnamed: D171.1 (K), U7.8 (OUT6)
unnamed: D72.1 (K), D172.2 (A)
unnamed: D172.1 (K), U7.9 (OUT7)
unnamed: D73.1 (K), D173.2 (A)
unnamed: D173.1 (K), U7.10 (OUT8)
unnamed: D74.1 (K), D174.2 (A)
unnamed: D174.1 (K), U7.11 (OUT9)
unnamed: D75.1 (K), D175.2 (A)
unnamed: D175.1 (K), U7.12 (OUT10)
unnamed: D76.1 (K), D176.2 (A)
unnamed: D176.1 (K), U7.13 (OUT11)
unnamed: D77.1 (K), D177.2 (A)
unnamed: D177.1 (K), U7.14 (OUT12)
unnamed: D78.1 (K), D178.2 (A)
unnamed: D178.1 (K), U7.15 (OUT13)
unnamed: D79.1 (K), D179.2 (A)
unnamed: D179.1 (K), U7.16 (OUT14)
unnamed: D80.1 (K), D180.2 (A)
unnamed: D180.1 (K), U7.17 (OUT15)
unnamed: D81.1 (K), D181.2 (A)
unnamed: D181.1 (K), U8.2 (OUT0)
unnamed: D82.1 (K), D182.2 (A)
unnamed: D182.1 (K), U8.3 (OUT1)
unnamed: D83.1 (K), D183.2 (A)
unnamed: D183.1 (K), U8.4 (OUT2)
unnamed: D84.1 (K), D184.2 (A)
unnamed: D184.1 (K), U8.5 (OUT3)
unnamed: D85.1 (K), D185.2 (A)
unnamed: D185.1 (K), U8.6 (OUT4)
unnamed: D86.1 (K), D186.2 (A)
unnamed: D186.1 (K), U8.7 (OUT5)
unnamed: D87.1 (K), D187.2 (A)
unnamed: D187.1 (K), U8.8 (OUT6)
unnamed: D88.1 (K), D188.2 (A)
unnamed: D188.1 (K), U8.9 (OUT7)
unnamed: D89.1 (K), D189.2 (A)
unnamed: D189.1 (K), U8.10 (OUT8)
unnamed: D90.1 (K), D190.2 (A)
unnamed: D190.1 (K), U8.11 (OUT9)
unnamed: D91.1 (K), D191.2 (A)
unnamed: D191.1 (K), U8.12 (OUT10)
unnamed: D92.1 (K), D192.2 (A)
unnamed: D192.1 (K), U8.13 (OUT11)
unnamed: D93.1 (K), D193.2 (A)
unnamed: D193.1 (K), U8.14 (OUT12)
unnamed: D94.1 (K), D194.2 (A)
unnamed: D194.1 (K), U8.15 (OUT13)
unnamed: D95.1 (K), D195.2 (A)
unnamed: D195.1 (K), U8.16 (OUT14)
unnamed: D96.1 (K), D196.2 (A)
unnamed: D196.1 (K), U8.17 (OUT15)
unnamed: D97.1 (K), D197.2 (A)
unnamed: D197.1 (K), U9.2 (OUT0)
unnamed: D98.1 (K), D198.2 (A)
unnamed: D198.1 (K), U9.3 (OUT1)
unnamed: D99.1 (K), D199.2 (A)
unnamed: D199.1 (K), U9.4 (OUT2)
unnamed: D200.1 (K), U9.5 (OUT3)
unnamed: D201.1 (K), D217.2 (A)
unnamed: D202.1 (K), D218.2 (A)
unnamed: D203.1 (K), D219.2 (A)
unnamed: D204.1 (K), D220.2 (A)
unnamed: D205.1 (K), D221.2 (A)
unnamed: D206.1 (K), D222.2 (A)
unnamed: D207.1 (K), D223.2 (A)
unnamed: D208.1 (K), D224.2 (A)
unnamed: D209.1 (K), D225.2 (A)
unnamed: D210.1 (K), D226.2 (A)
unnamed: D211.1 (K), D227.2 (A)
unnamed: D212.1 (K), D228.2 (A)
unnamed: D213.1 (K), D229.2 (A)
unnamed: D214.1 (K), D230.2 (A)
unnamed: D215.1 (K), D231.2 (A)
unnamed: D216.1 (K), D232.2 (A)
unnamed: D217.1 (K), U10.2 (OUT0)
unnamed: D218.1 (K), U10.3 (OUT1)
unnamed: D219.1 (K), U10.4 (OUT2)
unnamed: D220.1 (K), U10.5 (OUT3)
unnamed: D221.1 (K), U10.6 (OUT4)
unnamed: D222.1 (K), U10.7 (OUT5)
unnamed: D223.1 (K), U10.8 (OUT6)
unnamed: D224.1 (K), U10.9 (OUT7)
unnamed: D225.1 (K), U10.10 (OUT8)
unnamed: D226.1 (K), U10.11 (OUT9)
unnamed: D227.1 (K), U10.12 (OUT10)
unnamed: D228.1 (K), U10.13 (OUT11)
unnamed: D229.1 (K), U10.14 (OUT12)
unnamed: D230.1 (K), U10.15 (OUT13)
unnamed: D231.1 (K), U10.16 (OUT14)
unnamed: D232.1 (K), U10.17 (OUT15)
unnamed: D233.1 (K), D237.2 (A)
unnamed: D234.1 (K), D238.2 (A)
unnamed: D235.1 (K), D239.2 (A)
unnamed: D236.1 (K), D240.2 (A)
unnamed: D237.1 (K), U11.2 (OUT)
unnamed: D238.1 (K), U12.2 (OUT)
unnamed: D239.1 (K), U13.2 (OUT)
unnamed: D240.1 (K), U14.2 (OUT)
unnamed: D241.2 (A), R5.2
unnamed: D241.1 (K), U1.7 (~PGOOD)
unnamed: D242.2 (A), R6.2
unnamed: D242.1 (K), U1.9 (~CHG)
unnamed: D243.2 (A), R19.2
unnamed: J1.A5 (CC1), R2.2
unnamed: J1.B5 (CC2), R1.2
unnamed: JP1.2 (B), R23.1
unnamed: C2.1, R5.1, R6.1, SW1.1 (A), U1.5 (EN2), U1.10 (OUT), U1.11 (OUT)
unnamed: R22.2, U1.12 (ILIM)
unnamed: R3.2, R23.2, U1.16 (ISET)
unnamed: R4.1, U1.1 (TS)
unnamed: C18.1, SW3.2, U2.9 (PC2)
unnamed: R19.1, U2.10 (PC3)
unnamed: C7.1, SW2.1, U2.1 (PD7)
unnamed: R7.2, U3.20 (IREF)
unnamed: R8.2, U4.20 (IREF)
unnamed: R9.2, U5.20 (IREF)
unnamed: R10.2, U6.20 (IREF)
unnamed: R11.2, U7.20 (IREF)
unnamed: R12.2, U8.20 (IREF)
unnamed: R13.2, U9.20 (IREF)
unnamed: R14.2, U10.20 (IREF)
unnamed: R15.1, U11.6 (R_EXT)
unnamed: R16.1, U12.6 (R_EXT)
unnamed: R17.1, U13.6 (R_EXT)
unnamed: R18.1, U14.6 (R_EXT)
VBUS: C1.1, J1.A9 (VBUS), J1.B9 (VBUS), U1.13 (IN)
VCC: C4.1, C8.2, C9.2, C10.2, C11.2, C12.2, C13.2, C14.1, C15.2, D1.2 (A), D2.2 (A), D3.2 (A), D4.2 (A), D5.2 (A), D6.2 (A), D7.2 (A), D8.2 (A), D9.2 (A), D10.2 (A), D11.2 (A), D12.2 (A), D13.2 (A), D14.2 (A), D15.2 (A), D16.2 (A), D17.2 (A), D18.2 (A), D19.2 (A), D20.2 (A), D21.2 (A), D22.2 (A), D23.2 (A), D24.2 (A), D25.2 (A), D26.2 (A), D27.2 (A), D28.2 (A), D29.2 (A), D30.2 (A), D31.2 (A), D32.2 (A), D33.2 (A), D34.2 (A), D35.2 (A), D36.2 (A), D37.2 (A), D38.2 (A), D39.2 (A), D40.2 (A), D41.2 (A), D42.2 (A), D43.2 (A), D44.2 (A), D45.2 (A), D46.2 (A), D47.2 (A), D48.2 (A), D49.2 (A), D50.2 (A), D51.2 (A), D52.2 (A), D53.2 (A), D54.2 (A), D55.2 (A), D56.2 (A), D57.2 (A), D58.2 (A), D59.2 (A), D60.2 (A), D61.2 (A), D62.2 (A), D63.2 (A), D64.2 (A), D65.2 (A), D66.2 (A), D67.2 (A), D68.2 (A), D69.2 (A), D70.2 (A), D71.2 (A), D72.2 (A), D73.2 (A), D74.2 (A), D75.2 (A), D76.2 (A), D77.2 (A), D78.2 (A), D79.2 (A), D80.2 (A), D81.2 (A), D82.2 (A), D83.2 (A), D84.2 (A), D85.2 (A), D86.2 (A), D87.2 (A), D88.2 (A), D89.2 (A), D90.2 (A), D91.2 (A), D92.2 (A), D93.2 (A), D94.2 (A), D95.2 (A), D96.2 (A), D97.2 (A), D98.2 (A), D99.2 (A), D100.2 (A), D201.2 (A), D202.2 (A), D203.2 (A), D204.2 (A), D205.2 (A), D206.2 (A), D207.2 (A), D208.2 (A), D209.2 (A), D210.2 (A), D211.2 (A), D212.2 (A), D213.2 (A), D214.2 (A), D215.2 (A), D216.2 (A), D233.2 (A), D234.2 (A), D235.2 (A), D236.2 (A), J3.3, SW1.2 (B), U2.6 (VDD), U3.21 (VCC), U4.21 (VCC), U5.21 (VCC), U6.21 (VCC), U7.21 (VCC), U8.21 (VCC), U9.21 (VCC), U10.21 (VCC)

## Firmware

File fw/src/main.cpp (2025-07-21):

#include <Arduino.h>

// pin definitions
const int CLK_PIN = PD0;
const int RING_DATA_PIN = PD2;
const int RING_BLANK_PIN = PD3;
const int RING_LATCH_PIN = PC1;
const int COUNTER_DATA_PIN = PD5;
const int COUNTER_BLANK_PIN = PD4;
const int COUNTER_LATCH_PIN = PD6;
const int CORNER_ENABLE_PIN = PC0;
const int MODE_BUTTON_PIN = PC2;
const int MODE_LED_PIN = PC3;

// config
const int FREQ = 1000; // in hz
const int PERIOD = 100;
const int RING_BRIGHTNESS = 100; // 0-100%
const int COUNTER_BRIGHTNESS = 50;
const int CORNER_BRIGHTNESS = 100;

void update()
{
  static int ticks = 0;

  // generate clock signal
  digitalWrite(CLK_PIN, ticks % 2);

  if (ticks % 2 == 0)
  {
    // falling clock edge, do signal manipulation here
    digitalWrite(RING_DATA_PIN, ticks % (PERIOD * 2) == 0);
    int counter = (ticks - 1) / (PERIOD * 2) + 1;
    int index = (ticks / 2 + 15) % PERIOD;
    digitalWrite(COUNTER_DATA_PIN, counter >> index & 1);
  }

  // latch previously shifted counter into LED drivers
  digitalWrite(COUNTER_LATCH_PIN, ticks % (PERIOD * 2) == 1);

  ticks++;
}

void changeMode()
{
  static bool standby = false;
  standby = !standby;
  if (standby)
  {
    // turn off LEDs
    analogWrite(RING_BLANK_PIN, 4096);
    analogWrite(COUNTER_BLANK_PIN, 4096);
    analogWrite(CORNER_ENABLE_PIN, 0);
    digitalWrite(MODE_LED_PIN, HIGH);
  }
  else
  {
    // turn on LEDs with configured brightness
    analogWrite(RING_BLANK_PIN, (1 - RING_BRIGHTNESS / 100.0) * 4096);
    analogWrite(COUNTER_BLANK_PIN, (1 - COUNTER_BRIGHTNESS / 100.0) * 4096);
    analogWrite(CORNER_ENABLE_PIN, CORNER_BRIGHTNESS / 100.0 * 4096);
    digitalWrite(MODE_LED_PIN, LOW);
  }
}

void setup()
{
  // initialize IO
  pinMode(CLK_PIN, OUTPUT);
  pinMode(RING_DATA_PIN, OUTPUT);
  pinMode(RING_BLANK_PIN, OUTPUT);
  pinMode(RING_LATCH_PIN, OUTPUT);
  pinMode(COUNTER_DATA_PIN, OUTPUT);
  pinMode(COUNTER_BLANK_PIN, OUTPUT);
  pinMode(COUNTER_LATCH_PIN, OUTPUT);
  pinMode(CORNER_ENABLE_PIN, OUTPUT);
  pinMode(MODE_BUTTON_PIN, INPUT_PULLUP);
  pinMode(MODE_LED_PIN, OUTPUT);

  // set outputs to initial values
  digitalWrite(RING_DATA_PIN, LOW);
  digitalWrite(RING_BLANK_PIN, HIGH);
  digitalWrite(RING_LATCH_PIN, HIGH);
  digitalWrite(COUNTER_DATA_PIN, LOW);
  digitalWrite(COUNTER_BLANK_PIN, HIGH);
  digitalWrite(COUNTER_LATCH_PIN, HIGH);
  digitalWrite(MODE_LED_PIN, LOW);

  // set brightness using PWM
  analogWriteFrequency(8000); // set PWM frequency (internally sets frequency for Timer2)
  analogWrite(RING_BLANK_PIN, (1 - RING_BRIGHTNESS / 100.0) * 4096);
  analogWrite(COUNTER_BLANK_PIN, (1 - COUNTER_BRIGHTNESS / 100.0) * 4096);
  analogWrite(CORNER_ENABLE_PIN, CORNER_BRIGHTNESS / 100.0 * 4096);

  // clear shift registers
  for (int i = 0; i < PERIOD; i++)
  {
    digitalWrite(CLK_PIN, LOW);
    delayMicroseconds(10);
    digitalWrite(CLK_PIN, HIGH);
    delayMicroseconds(10);
  }

  // attach button IRQ
  attachInterrupt(MODE_BUTTON_PIN, GPIO_Mode_IPU, &changeMode, EXTI_Mode_Interrupt, EXTI_Trigger_Falling);

  // configure Timer1 and attach IRQ
  HardwareTimer *timer1 = new HardwareTimer(TIM1);
  timer1->setOverflow(FREQ * 2, HERTZ_FORMAT);
  timer1->attachInterrupt(update);
  timer1->resume();
}

void loop() {}

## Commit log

2024-09-12 schematics: add note about step-up regulator
    [RocSync_testing.kicad_sch]
2024-09-12 sw: fix frame export
2024-09-12 sw: make threads terminate on exit
2024-09-13 sw: fix debug and frame export
2024-09-13 hw: add latest 3d models
    [RocSync.f3d, cover.step, cover_bottom.stl, cover_top.stl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]
2024-11-15 dont crash on skipped frame
2024-11-18 improve result printing
2024-11-18 output regression error for every considered frame
2024-11-19 force regression to use > 80% of samples
2025-05-04 add more conditions to consider a frame & allow negative timecodes for windows
2025-07-10 New folder evaluation that contains frame extraction script including guidelines + the manual synchronization script including the guidelines.
2025-07-22 [sw] use dynamic LED thresholding & tune blob detection params
2025-07-23 [sw] disable blob inertia filter for now
